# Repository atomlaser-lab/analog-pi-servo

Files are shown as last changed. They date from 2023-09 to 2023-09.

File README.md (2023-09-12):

# Analog PI controller

## Features

   This device implementes a PI controller, with integrator
   reset. The polarity of the reset signal is selectable by choosing
   which of R11, R12 to populate.

## Layout
   PDF copies of the schmatic and PCB are found in the *Generated* folder

## Manufacture and ordering
   Gerber files are included in this repo under the directory CAM/ and under the archive CAM.zip.  Use any PCB manufacturer; a reliable and quick one out of China is JLC-PCB.

   The bill of materials can be found under the CSV text file "LaserPID.txt".  You can import this directly into Digikey.com.  The quantities are set for creating 5 boards.  You may want to add sockets for the op-amps and stand-offs for the boards when ordering.  If the INA105 is not available, you can use the INA106.

## Soldering
   All parts should be able to be soldered without much trouble.  A web-page has been created to check off parts as they are soldered.  The web-page can be created from the bill of materials (LaserPID.txt) using `python3 generate-web-page.py LaserPID.txt`.  Open the HTML file "PartList.html" in any web-browser.

## Notes
   The value of R6 and C6 should be set by the user for their particular application.  Keeping R6 as 3.3k and setting C7 as 10 nF seems to work well in controlling dipole laser powers.

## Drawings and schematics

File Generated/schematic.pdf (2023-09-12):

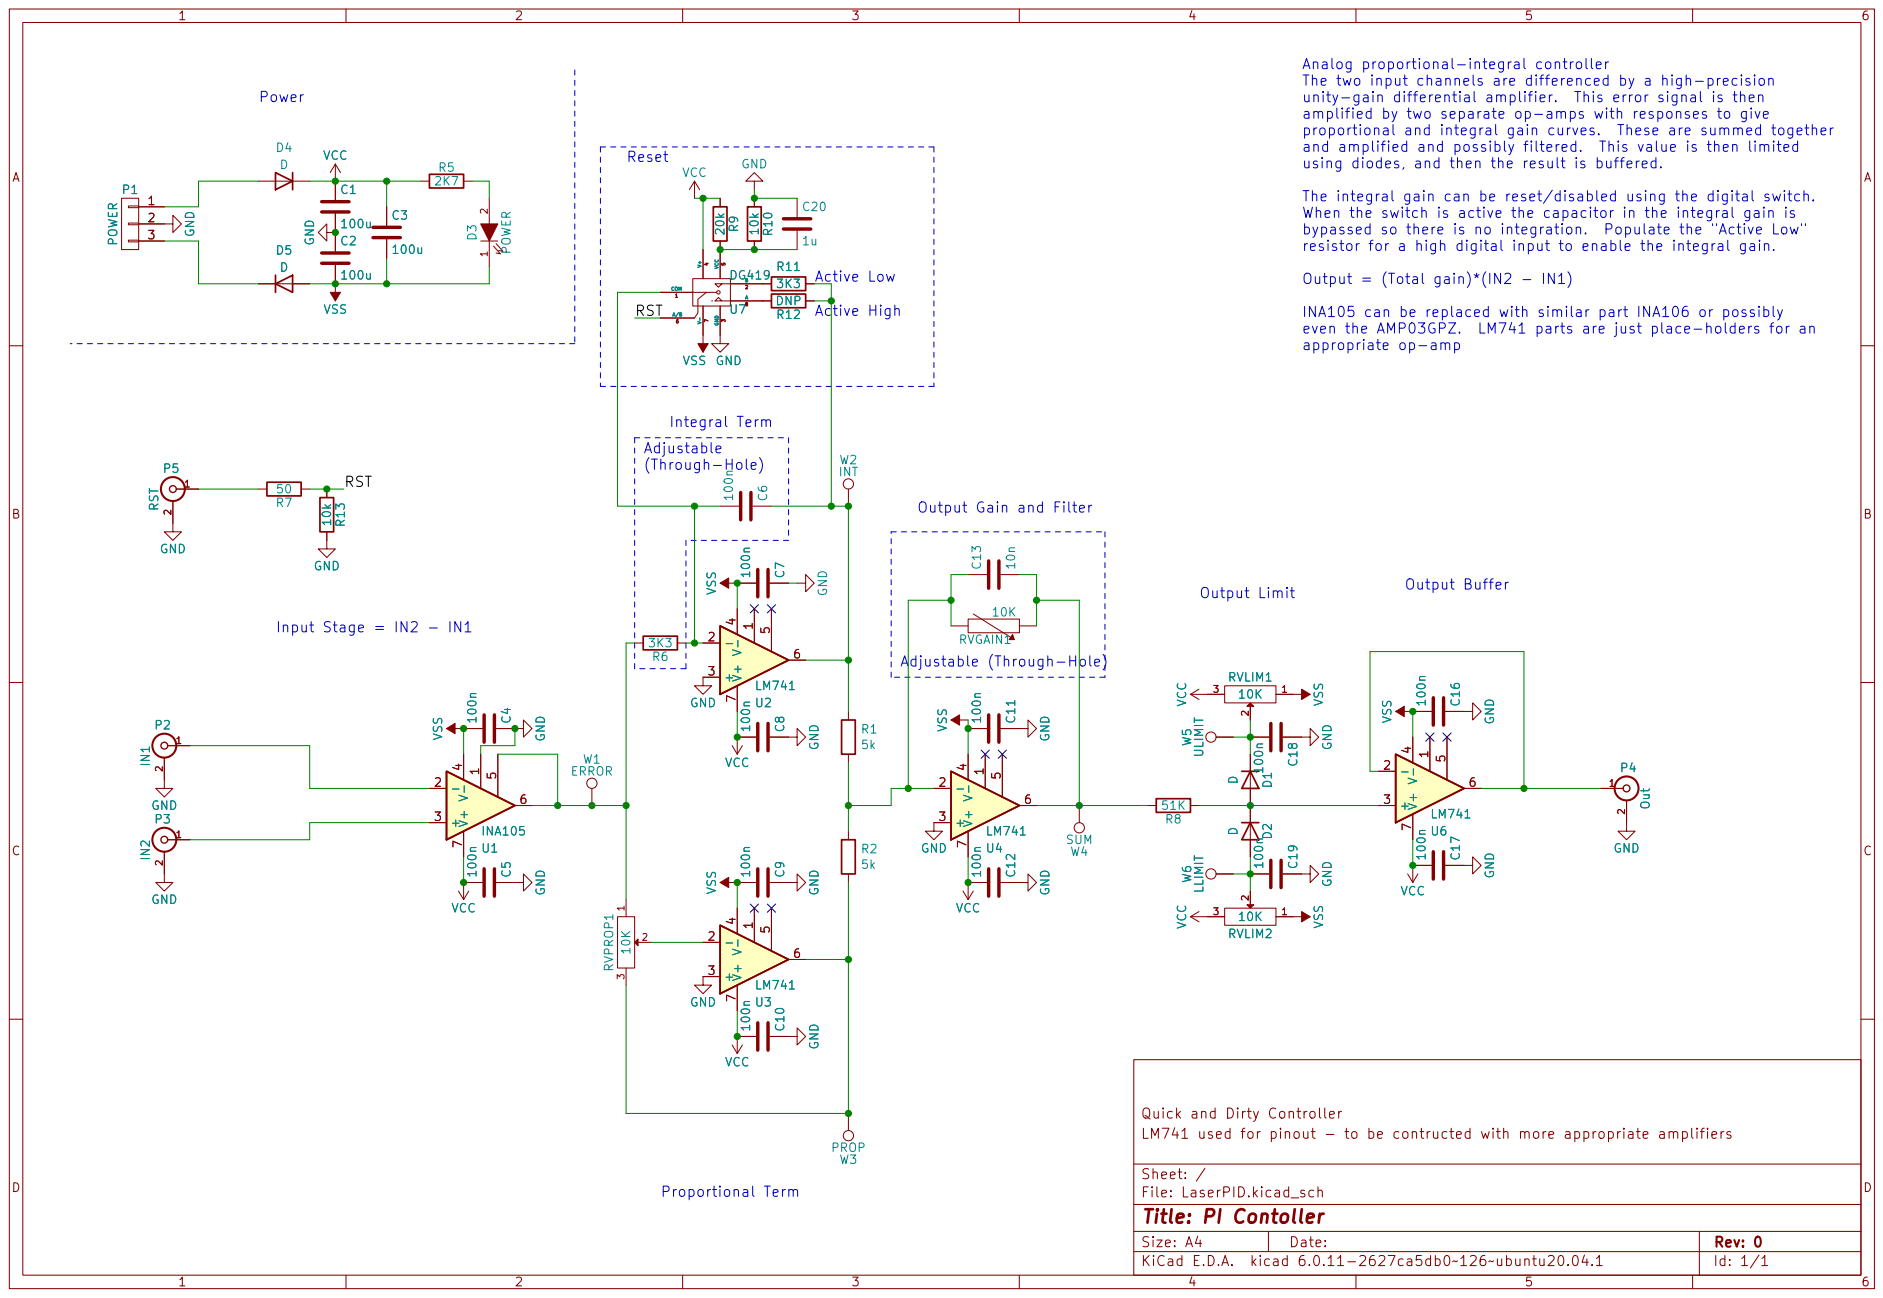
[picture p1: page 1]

2 P5 RST 10k R13 GND W4 SUM GND100n C5 VCC GND 100n C7

7 VCC GND GND VSS100n C4 GND GND

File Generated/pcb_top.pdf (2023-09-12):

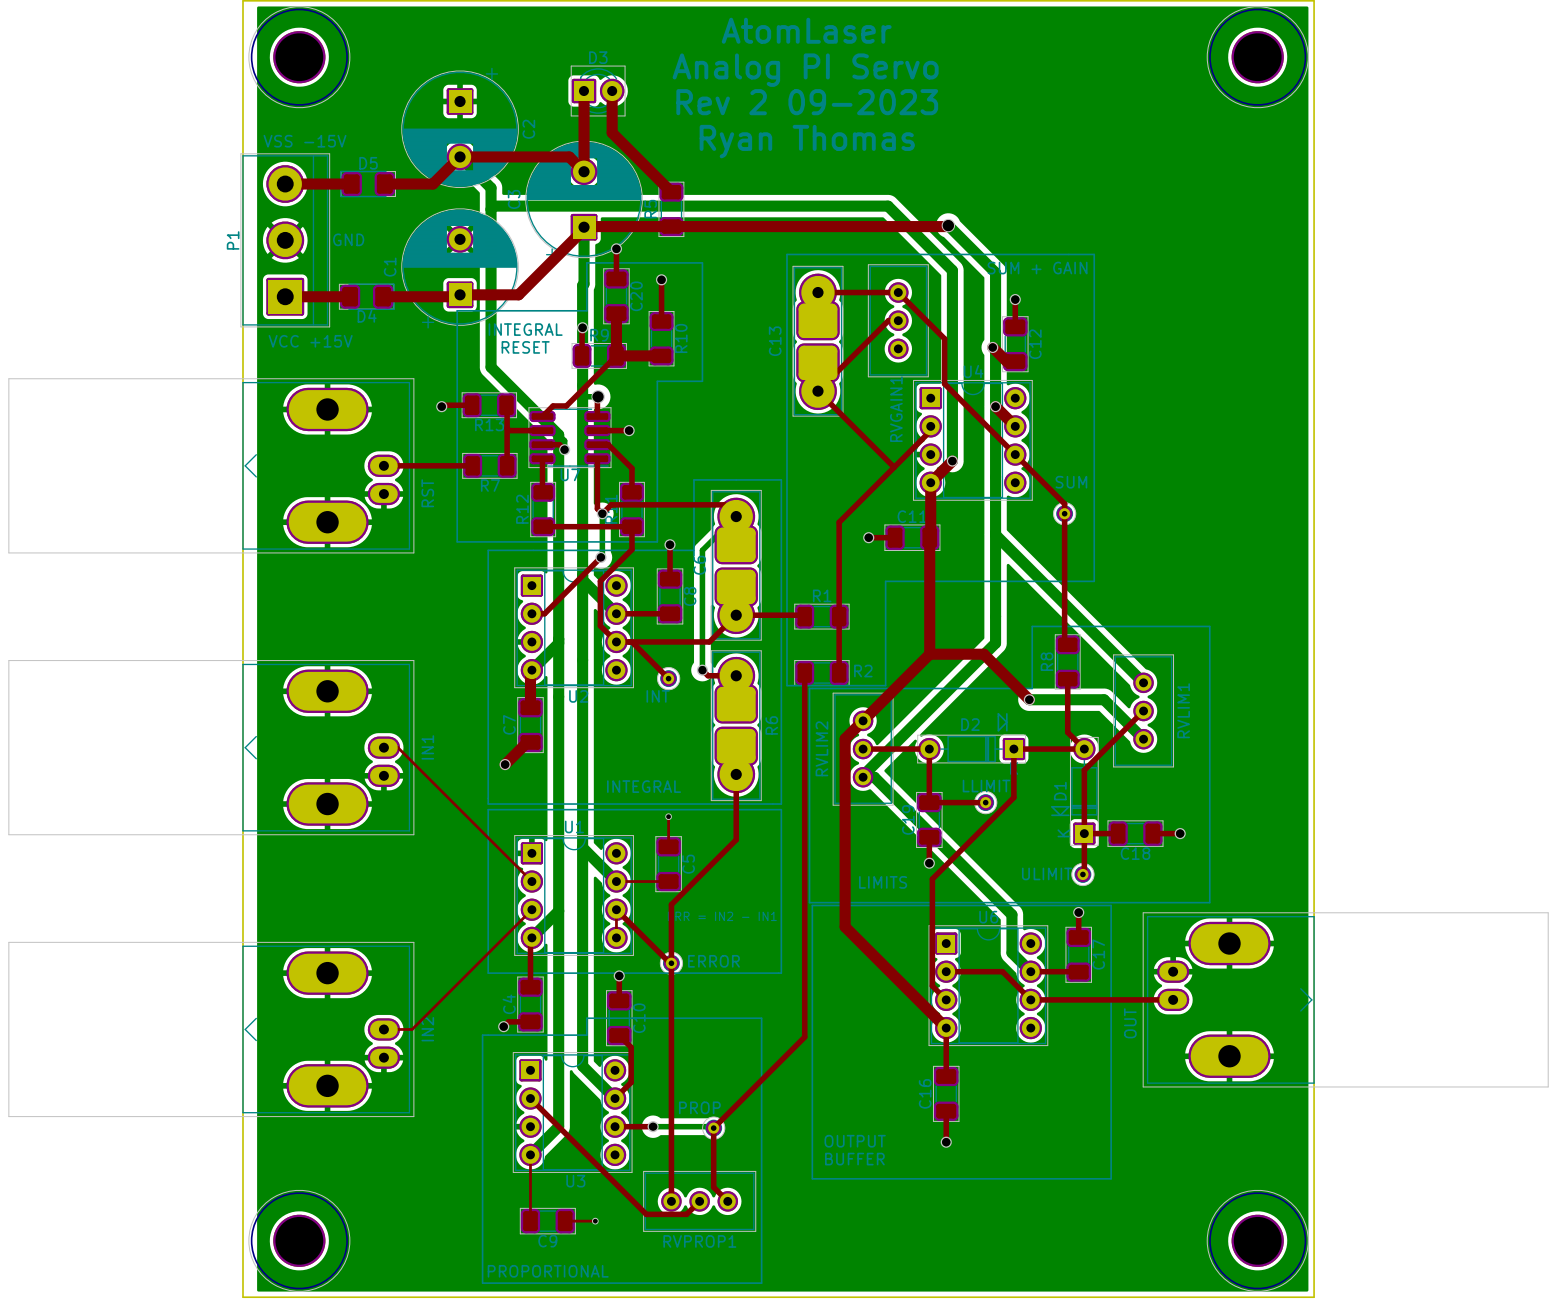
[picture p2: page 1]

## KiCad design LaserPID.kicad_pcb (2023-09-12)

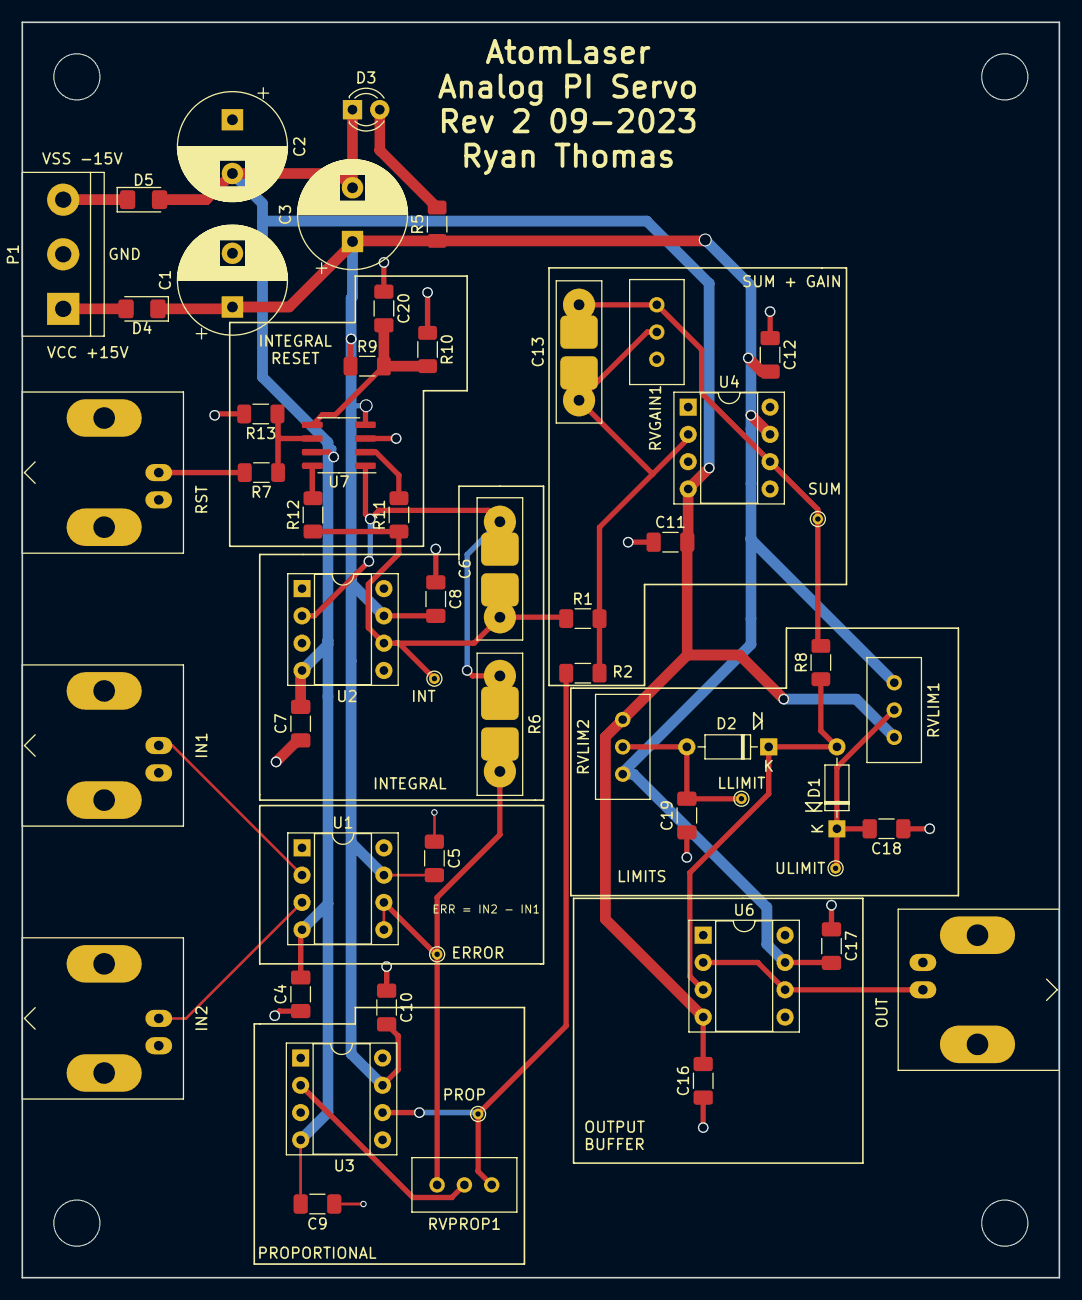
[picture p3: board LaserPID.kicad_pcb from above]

Board: 2 copper layers, 96.5 x 116.8 mm, 55 parts (0 on the bottom side), 24 nets.

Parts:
C1, C2, C3: 100u; CP_Radial_D10.0mm_P5.00mm
C4, C5, C7, C8, C9, C10, C11, C12, C16, C17, C18, C19: 100n; C_1206_3216Metric_Pad1.33x1.80mm_HandSolder
C6: 100n; R_Universal_L13.0mm_W4.0mm_P9.00mm
C13: 10n; R_Universal_L13.0mm_W4.0mm_P9.00mm
C20: 1u; C_1206_3216Metric_Pad1.33x1.80mm_HandSolder
D1, D2: D; D_DO-35_SOD27_P7.62mm_Horizontal
D3: POWER; LED_D3.0mm
D4, D5: D; D_1206_3216Metric_Pad1.42x1.75mm_HandSolder
ERROR: ERROR; TestPoint_THTPad_D1.0mm_Drill0.5mm
IN1: IN1; BNC_Amphenol_B6252HB-NPP3G-50_Horizontal
IN2: IN2; BNC_Amphenol_B6252HB-NPP3G-50_Horizontal
INT: INT; TestPoint_THTPad_D1.0mm_Drill0.5mm
LLIMIT: LLIMIT; TestPoint_THTPad_D1.0mm_Drill0.5mm
OUT: Out; BNC_Amphenol_B6252HB-NPP3G-50_Horizontal
P1: POWER; TerminalBlock_bornier-3_P5.08mm
PROP: PROP; TestPoint_THTPad_D1.0mm_Drill0.5mm
R1, R2: 5k; R_1206_3216Metric_Pad1.30x1.75mm_HandSolder
R5: 2K7; R_1206_3216Metric_Pad1.30x1.75mm_HandSolder
R6: 3K3; R_Universal_L13.0mm_W4.0mm_P9.00mm
R7: 50; R_1206_3216Metric_Pad1.30x1.75mm_HandSolder
R8: 51K; R_1206_3216Metric_Pad1.30x1.75mm_HandSolder
R9: 20k; R_1206_3216Metric_Pad1.30x1.75mm_HandSolder
R10, R13: 10k; R_1206_3216Metric_Pad1.30x1.75mm_HandSolder
R11: 3K3; R_1206_3216Metric_Pad1.30x1.75mm_HandSolder
R12: DNP; R_1206_3216Metric_Pad1.30x1.75mm_HandSolder
RST: RST; BNC_Amphenol_B6252HB-NPP3G-50_Horizontal
RVGAIN1: 10K; Potentiometer_Bourns_3296W_Vertical
RVLIM1, RVLIM2: 10K; Potentiometer_Bourns_3296W_Vertical
RVPROP1: 10K; Potentiometer_Bourns_3296W_Vertical
SUM: SUM; TestPoint_THTPad_D1.0mm_Drill0.5mm
U1: INA105; DIP-8_W7.62mm_Socket
U2, U3, U4, U6: LM741; DIP-8_W7.62mm_Socket
U7: DG419; SOIC-8_3.9x4.9mm_P1.27mm
ULIMIT: ULIMIT; TestPoint_THTPad_D1.0mm_Drill0.5mm

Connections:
/RST: R7.1, R13.1, U7.6 (A/B)
GND: C1.2, C2.1, C4.1, C5.1, C7.1, C8.1, C9.1, C10.1, C11.1, C12.1, C16.1, C17.1, C18.1, C19.1, C20.1, IN1.2 (Ext), IN2.2 (Ext), OUT.2 (Ext), P1.2, R10.1, R13.2, RST.2 (Ext), U1.1, U2.3 (+), U3.3 (+), U4.3 (+), U7.3 (GND)
unnamed: C6.1, INT.1, R1.1, R11.1, R12.1, U2.6
unnamed: C6.2, R6.1, U2.2 (-), U7.1 (COM)
unnamed: C13.1, R1.2, R2.1, RVGAIN1.2, U4.2 (-)
unnamed: C13.2, R8.2, RVGAIN1.1, SUM.1, U4.6
unnamed: C18.2, D1.1 (K), RVLIM1.2, ULIMIT.1
unnamed: C19.2, D2.2 (A), LLIMIT.1, RVLIM2.2
unnamed: C20.2, R9.2, R10.2, U7.5 (VCC)
unnamed: D1.2 (A), D2.1 (K), R8.1, U6.3 (+)
unnamed: D3.2 (A), R5.2
unnamed: D4.2 (A), P1.1
unnamed: D5.1 (K), P1.3
unnamed: IN1.1 (In), U1.2 (-)
unnamed: IN2.1 (In), U1.3 (+)
unnamed: OUT.1 (In), U6.2 (-), U6.6
unnamed: R7.2, RST.1 (In)
unnamed: PROP.1, R2.2, RVPROP1.3, U3.6
unnamed: ERROR.1, R6.2, RVPROP1.1, U1.5, U1.6
unnamed: R11.2, U7.2 (B)
unnamed: R12.2, U7.8 (A)
unnamed: RVPROP1.2, U3.2 (-)
VCC: C1.1, C3.1, C5.2, C8.2, C10.2, C12.2, C17.2, D4.1 (K), R5.1, R9.1, RVLIM1.3, RVLIM2.3, U1.7 (V+), U2.7 (V+), U3.7 (V+), U4.7 (V+), U6.7 (V+), U7.4 (V+)
VSS: C2.2, C3.2, C4.2, C7.2, C9.2, C11.2, C16.2, D3.1 (K), D5.2 (A), RVLIM1.1, RVLIM2.1, U1.4 (V-), U2.4 (V-), U3.4 (V-), U4.4 (V-), U6.4 (V-), U7.7 (V-)

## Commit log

2016-11-14 As manufactured
    [LaserPID-B.Cu.gbl, LaserPID-B.Mask.gbs, LaserPID-B.SilkS.gbo, LaserPID-Edge.Cuts.gm1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]
2021-04-16 Rescued symbols, updated design, added digikey part numbers
    [LaserPID.kicad_pcb, LaserPID.sch]
2021-04-16 Re-made PCB with Kicad 5 foot print libraries
    Digikey part numbers now assigned
    [LaserPID.kicad_pcb, LaserPID.sch]
2021-06-03 Changed some part numbers, minor changes to PCB
    [LaserPID.kicad_pcb, LaserPID.sch]
2021-06-28 Minor updates to schematic and parts list
    [LaserPID-2021-04-06-07-57-53.sch, LaserPID-B.Cu.gbl, LaserPID-B.Mask.gbs, LaserPID-B.SilkS.gbo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]
2021-06-28 Added gerber files
    [LaserPID-B_Cu.gbr, LaserPID-B_Mask.gbr, LaserPID-B_Paste.gbr, LaserPID-B_SilkS.gbr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]
2021-08-12 Updates to board and parts list to correct some errors
    [LaserPID.kicad_pcb, LaserPID.sch]
2021-08-12 Added web-page for soldering, updated plots
    Added new web-page for keeping track of soldering parts on the board
    Python file generate-web-page.py uses the input text BOM to create
    the page.
    Updated generated pdf and gerber files
    [LaserPID-B_Cu.gbr, LaserPID-B_Mask.gbr, LaserPID-B_Paste.gbr, LaserPID-B_SilkS.gbr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]
2023-09-12 Updated to KiCAD 6, added input protection diodes, changed filter cap footprints
    [LaserPID.kicad_pcb, LaserPID.kicad_sch]
2023-09-12 Updated CAM/ and Generated/
    [LaserPID-B_Cu.gbr, LaserPID-B_Mask.gbr, LaserPID-B_Paste.gbr, LaserPID-B_Silkscreen.gbr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]
